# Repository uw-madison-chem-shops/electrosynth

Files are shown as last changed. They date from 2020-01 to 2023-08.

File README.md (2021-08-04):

# electrosynth 

Inexpensive circuits made for multi-channel electrochemical synthesis.
Galvanosynth: constant current driver.
Electrosynth: constant potential driver.

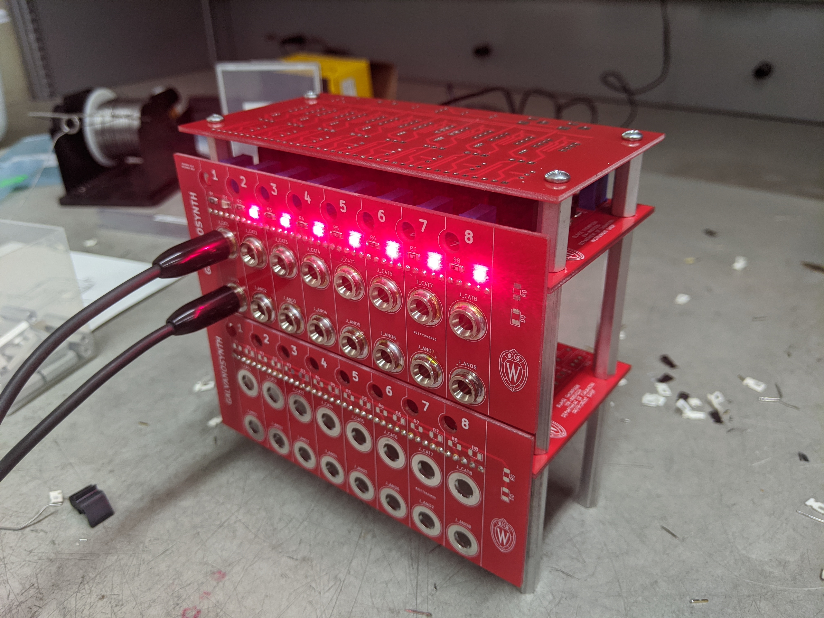
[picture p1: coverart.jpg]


## Repository

This is an open source hardware project licensed under the CERN Open Hardware Licence Version 2 - Permissive.
Please see the LICENSE file for the complete license.

This repository is being mirrored to several version control systems in an attempt to ensure maximum avaliability.

| name             | url                                                                  |
| ---------------- | -------------------------------------------------------------------- |
| blaise           | http://git.blaise.zone/uw-madison-chem-shops/electrosynth.git/about/ |
| Codeberg         | https://codeberg.org/uw-madison-chem-shops/electrosynth              |
| GitHub (primary) | https://github.com/uw-madison-chem-shops/electrosynth                |
| GitLab           | https://gitlab.com/uw-madison-chem-shops/electrosynth                |

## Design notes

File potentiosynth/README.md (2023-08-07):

# potentiosynth 

An inexpensive circuit made for driving multiple electrochemical constant potential reactions.



Each potentiosynth is made of three custom components:

- the main driver PCB
- the front panel PCB
- 3D printed bracket

See subdirectories for detailed instructions on each of these components.

## Bill of Materials

| reference      | value         | manufacturer  | part number          | vendors | # per Board |
| :------------- | :------------ | :------------ | :------------------- | :------ | :----------  |
| 40 Pin Header, Male, Right Angle | $0.00 | 3M | 2340-5111TG | Newark | 1 |
| 2" Standoff | $1.75 | Keystone Electronics | :------ | Newark | 4 |
| 0.625" Standoff | $0.50 | Keystone Electronics | :------ | Newark | 4 |

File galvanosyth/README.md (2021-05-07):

# galvanosynth

An inexpensive circuit made for driving multiple electrochemical constant current reactions.



Each galvanosynth is made of three custom components:

- the main driver PCB
- the front panel PCB
- 3D printed bracket

See subdirectories for detailed instructions on each of these components.

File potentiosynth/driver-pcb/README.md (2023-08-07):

# potentiosynth driver-pcb

An inexpensive circuit made for driving multiple electrochemical constant potential reactions.

## PCB

This PCB was designed using [KiCAD](https://www.kicad.org/) version 5.
Refer to [potentiosynth.pdf](./potentiosynth.pdf) for schematic. 
PCB images generated with [tracespace](https://github.com/tracespace/tracespace) follow.




## Bill of Materials

| reference      | value         | manufacturer  | part number          | vendors | # Per Board |
| :------------- | :------------ | :------------ | :------------------- | :------ | :--------- |
| 3/8 ˝ Square Trimpot® Trimming Potentiometer | $3.00 | Bourns | 3296X-1-202LF | DigiKey | 8 |
| Low-power Operational Amplifier  | $2.00  | Texas Instruments | TLV9154IDR | DigiKey | 8 |
| Fuse Block  | $3.00  | Littelfuse | 01550900M | DigiKey | 1 |
| 1 Amp Fuse  | $2.00  | Littelfuse | 0451001.MRL | DigiKey | 1 |
| PC TEST POINT MULTIPURPOSE RED  | $0.50  | Keystone Electronics | 5010 | Newark | 1 |
| PC TEST POINT MULTIPURPOSE BLACK  | $0.50  | Keystone Electronics | 5011 | Newark | 1 |
| Barrel Jack - 2.1 mm  | $0.50  | CUI | PJ-002A | DigiKey | 2 |
| 1/4W 4x 1k Resistors - 1206 | :------ | :------------ | :-------------- | :------ | 8 |
| 1/4W 4x 100k Resistors - 1206 | :------ | :------------ | :-------------- | :------ | 8 |
| 100 nF Capacitor - 1206 | :------ | :------------ | :-------------- | :------ | 1 |
| 330 nF Capacitor - 1206 | :------ | :------------ | :-------------- | :------ | 1 |
| 100 uF Capacitor - 1206 | :------ | :------------ | :-------------- | :------ | 1 |
| 1 uF Capacitor - 1206 | :------ | :------------ | :-------------- | :------ | 8 |
| R-7B15 - 0.5 | :------ | :------------ | :-------------- | :------ | 1 |

All prices are extended.
PCB itself should cost around $5.

## Changelog

### Unprinted

### Revision C

Added
- capacitor makes error detection better when unloaded
- bipolar error detection

### Revision B

Changed
- added fuse

Fixed
- added buffer amplifier since the differential amplifier drew too much current from reference

### Revision A 

Changed
- initial design

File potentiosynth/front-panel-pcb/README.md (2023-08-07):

# potentiosynth front-panel-pcb

An inexpensive circuit made for driving multiple electrochemical constant potential reactions.

## PCB

This PCB was designed using [KiCAD](https://www.kicad.org/) version 5.
Refer to [front-panel.pdf](./front-panel.pdf) for schematic. 
PCB images generated with [tracespace](https://github.com/tracespace/tracespace) follow.




## Bill of Materials

| reference      | value         | manufacturer  | part number          | vendors | # per Board |
| :------------- | :------------ | :------------ | :------------------- | :------ | :----------  |
| Banana Jack Board Mount | $1.00 | Keystone Electronics | 575-4 | Newark | 24 |
| 40 Pin Header, Male, Right Angle | $0.00 | 3M | 2340-5111TG | N/A | 1 (Cut down to 3 pins)  |
| 0.1" Jumper - 2 Position | $0.00 | Multicomp | MC-2228CG | N/A | 1 |
| 1/4W 1k Resistors - 1206 | :----- | :------------ | :-------- | :------ | 11 |
| SMT LEDs - 1206 | :----- | :------------ | :-------- | :------ | 11  |

All prices are extended.
PCB itself should cost around $5.

## Changelog

### Unprinted

## Fixed
- fixed silkscreen labels for oxidation and reduction

### Revision A 

## Changed
- initial design

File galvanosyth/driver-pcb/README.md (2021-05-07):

# galvanosynth driver-pcb

An inexpensive circuit made for driving multiple electrochemical constant current reactions.

## PCB

This PCB was designed using [KiCAD](https://www.kicad.org/) version 5.
Refer to [galvanosynth.pdf](./galvanosynth.pdf) for schematic. 
PCB images generated with [tracespace](https://github.com/tracespace/tracespace) follow.




## Bill of Materials

parts "per layer" for galvanosynth

| reference      | value         | manufacturer  | part number          | vendors |
| :------------- | :------------ | :------------ | :------------------- | :------ |
| trim pot, 2k                | 3296X-1-202LF       | 2.50 |     8 | 20.00 |         |
| banana jack                 | 575-4               | 1.00 |    16 | 16.00 |         |
| transistor, power           | IRF630              | 1.50 |     8 | 12.00 |         |
| PCB, mother                 | (custom)            | 6.00 |     1 |  6.00 |         |
| PCB, daughter               | (custom)            | 6.00 |     1 |  6.00 |         |
| standoff, 2", stacking      | 4558-440-AL         | 1.50 |     4 |  6.00 |         |
| op amp                      | LM358AP             | 0.50 |     8 |  4.00 |         |
| transistor, signal          | 2N7000              | 0.25 |     8 |  4.00 |         |
| bracket                     | (3D printed)        | 2.00 |     2 |  4.00 |         |
| trim pot, 1k                | 3296X-1-102LF       | 2.50 |     1 |  2.50 |         |
| barrel jack                 | PJ-002A             | 1.00 |     2 |  2.00 |         |
| LED, red                    | LTST-C230KRKT       | 0.25 |     8 |  2.00 |         |
| 100 uF                      | C3216X5R1A107M160AC | 1.25 |     1 |  1.25 |         |
| header, 40 pin, right angle | PRPC040SGAN-M71RC   | 1.00 |     1 |  1.00 |         |
| voltage regulator           | L7815CV             | 0.50 |     1 |  0.50 |         |
| test point, red             | 5010                | 0.50 |     1 |  0.50 |         |
| test point, white           | 5012                | 0.50 |     1 |  0.50 |         |
| test point, yellow          | 5014                | 0.50 |     1 |  0.50 |         |
| 330 nF                      | CC1206JRX7R9BB334   | 0.25 |     1 |  0.25 |         |
| LED, green                  | LTST-C150GKT        | 0.25 |     1 |  0.25 |         |
| 100 nF                      | CC1206KRX7R9BB104   | 0.10 |     1 |  0.10 |         |
| 10 kΩ                       | RC1206FR-0710KL     | 0.00 |     1 |  0.00 |         |
| 47 Ω                        | RC1206FR-0747RL     | 0.00 |     1 |  0.00 |         |
| 1 kΩ                        | RC1206FR-071KL      | 0.00 |    24 |  0.00 |         |
| 100 kΩ                      | RC1206FR-07100KL    | 0.00 |    16 |  0.00 |         |
| 10 Ω                        | RC1206FR-0710RL     | 0.00 |     8 |  0.00 |         |

All prices are extended.
PCB itself should cost around $5.

## Changelog

### Unprinted

### Revision D 

Changed
- initial design

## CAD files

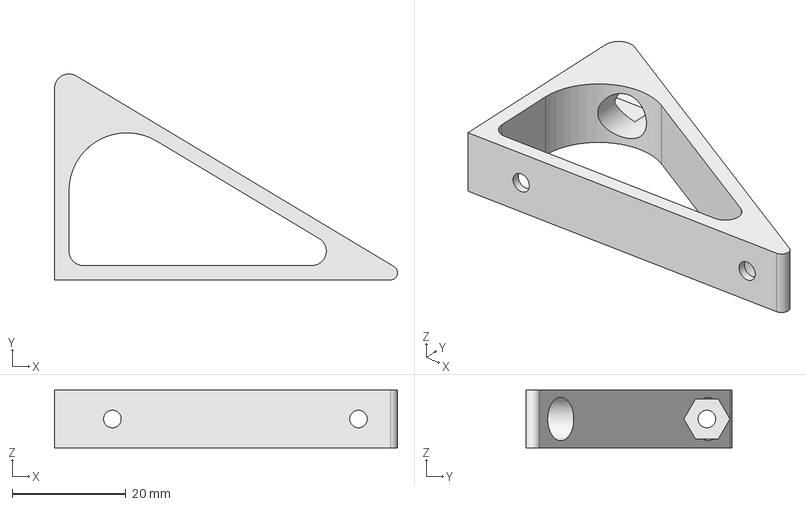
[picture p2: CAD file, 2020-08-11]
potentiosynth/bracket/bracket.FCStd
60.2 x 36.2 x 10.2 mm

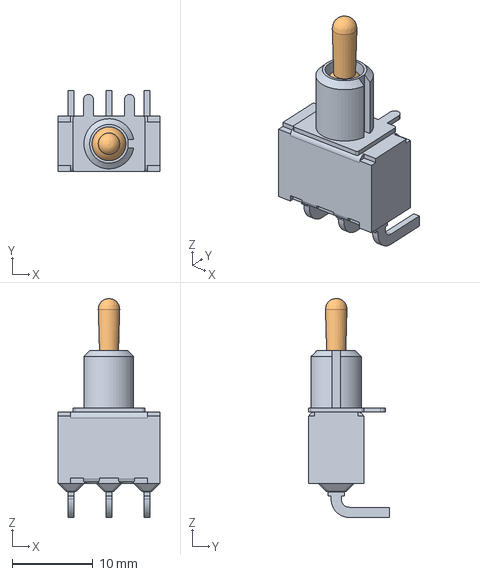
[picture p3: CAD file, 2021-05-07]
potentiosynth/front-panel-pcb/kicad/models/100SP1T2B4M6QE.step
12.7 x 10.0 x 27.2 mm

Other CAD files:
potentiosynth/bracket/bracket.stl

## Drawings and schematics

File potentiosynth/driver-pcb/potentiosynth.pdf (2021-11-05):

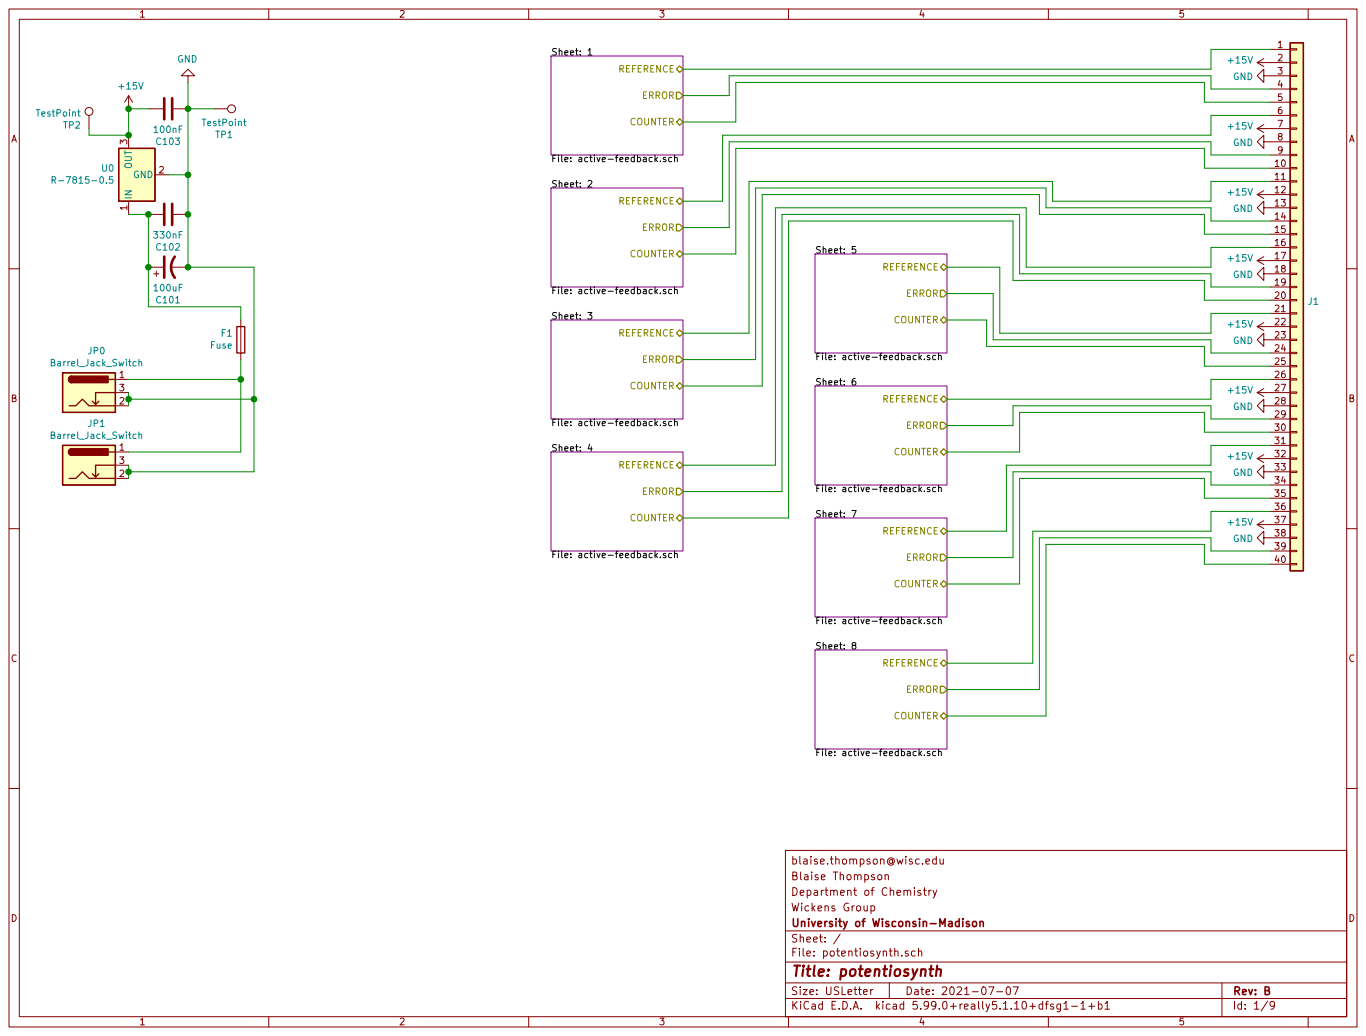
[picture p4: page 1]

Sheet: 1 File: active-feedback.schERROR

Sheet: 2 File: active-feedback.schERROR

Sheet: 5 File: active-feedback.schERROR
blaise.thompson@wisc.edu Sheet: 7 File: active-feedback.schERROR

Sheet: 3 File: active-feedback.schERROR

Sheet: 6 File: active-feedback.schERROR

Sheet: 4 File: active-feedback.schERROR

Sheet: 8 File: active-feedback.schERROR

Blaise Thompson
Department of Chemistry
Wickens Group
File: potentiosynth.sch Sheet: / University of Wisconsin-Madison

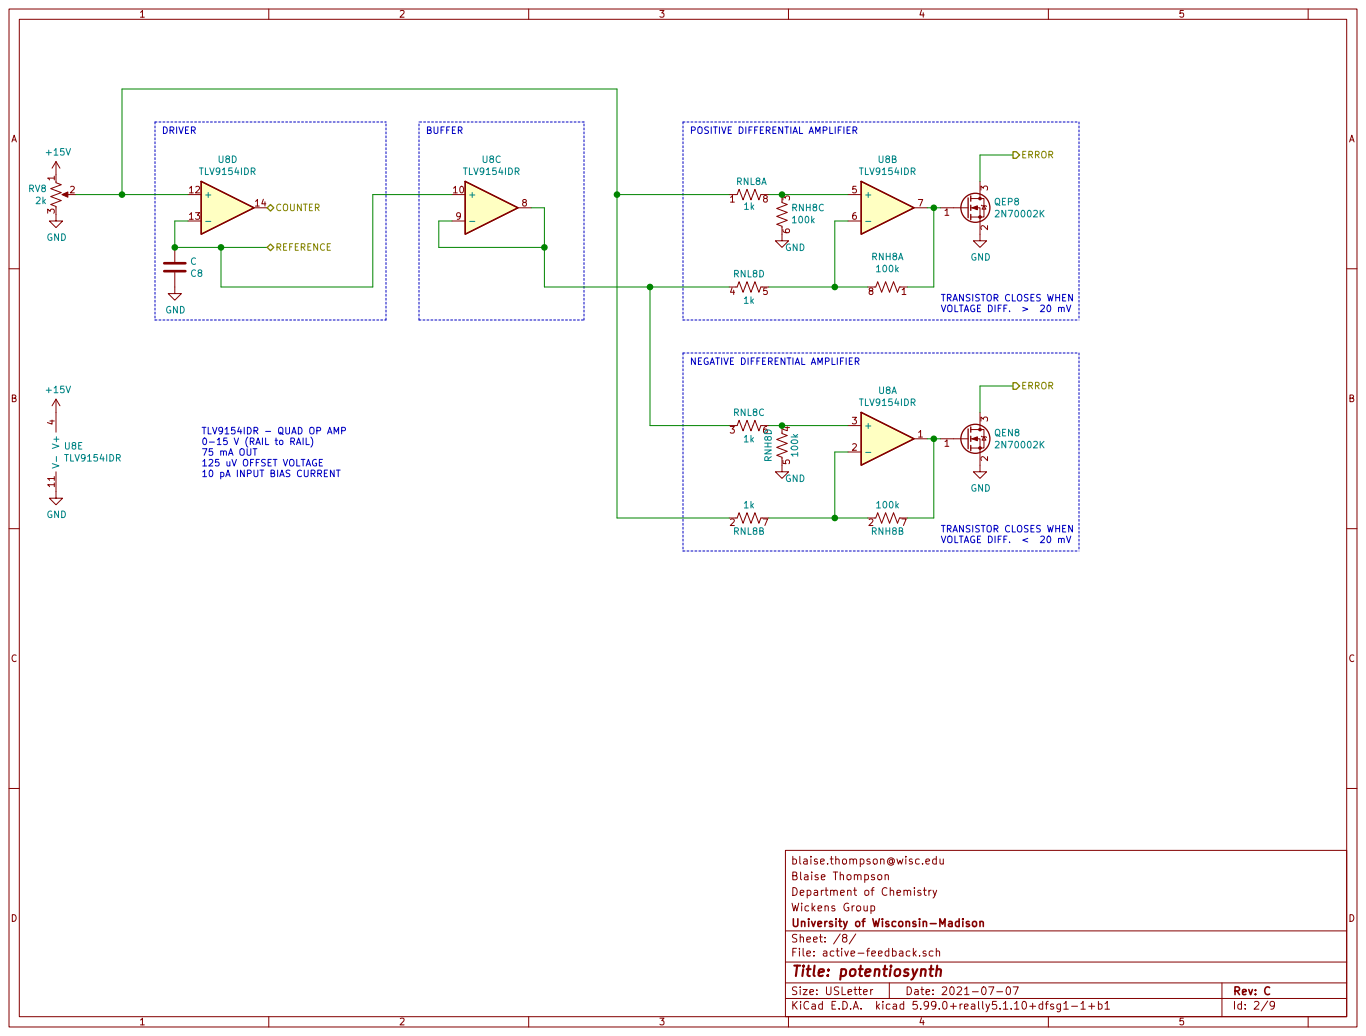
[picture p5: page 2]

TRANSISTOR CLOSES WHEN
VOLTAGE DIFF. > 20 mV TRANSISTOR CLOSES WHEN

VOLTAGE DIFF. < 20 mV TLV9154IDR - QUAD OP AMP
0-15 V (RAIL to RAIL) 75 mA OUT

Blaise Thompson
Department of Chemistry
Wickens Group
File: active-feedback.sch Sheet: /8/ University of Wisconsin-Madison

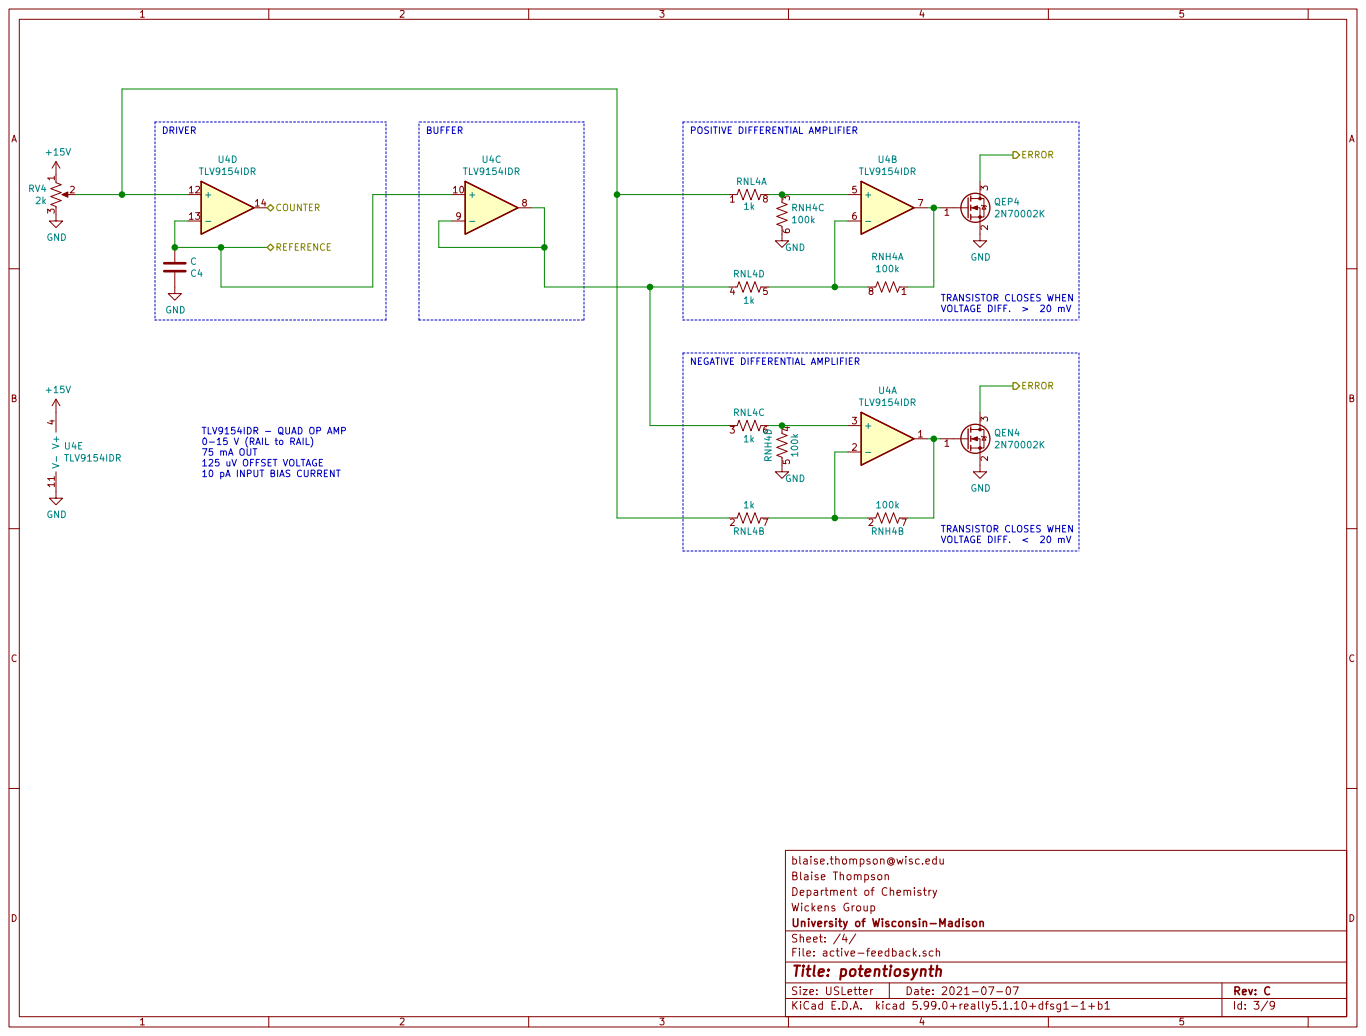
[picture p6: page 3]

TRANSISTOR CLOSES WHEN
VOLTAGE DIFF. > 20 mV TRANSISTOR CLOSES WHEN

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

Blaise Thompson
Department of Chemistry
Wickens Group
File: active-feedback.sch Sheet: /4/ University of Wisconsin-Madison

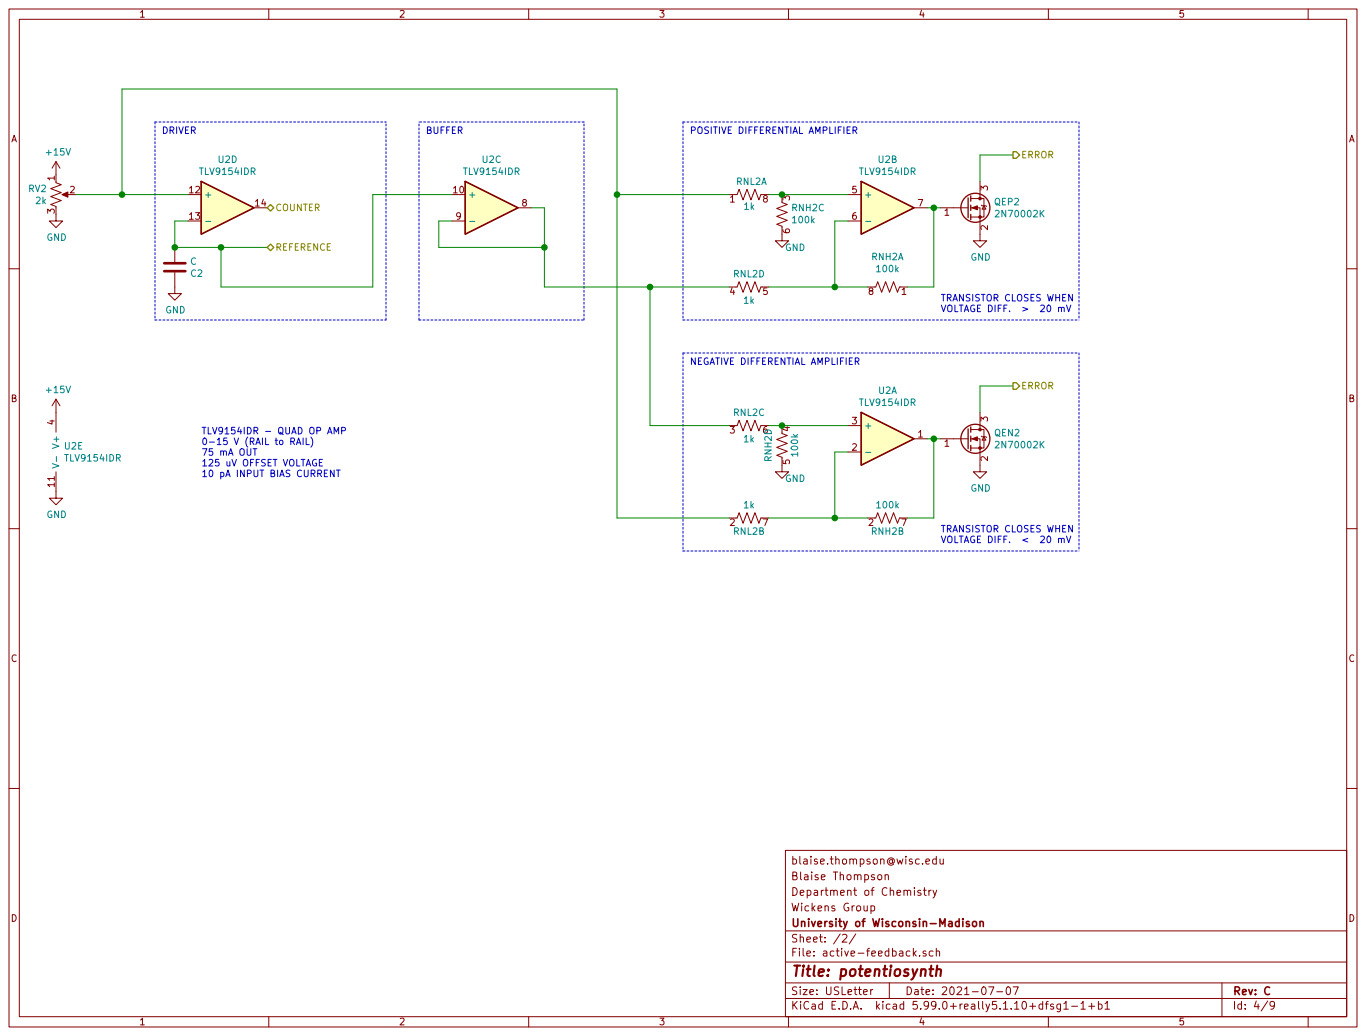
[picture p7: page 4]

TRANSISTOR CLOSES WHEN
VOLTAGE DIFF. > 20 mV TRANSISTOR CLOSES WHEN

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

Blaise Thompson
Department of Chemistry
Wickens Group
File: active-feedback.sch Sheet: /2/ University of Wisconsin-Madison

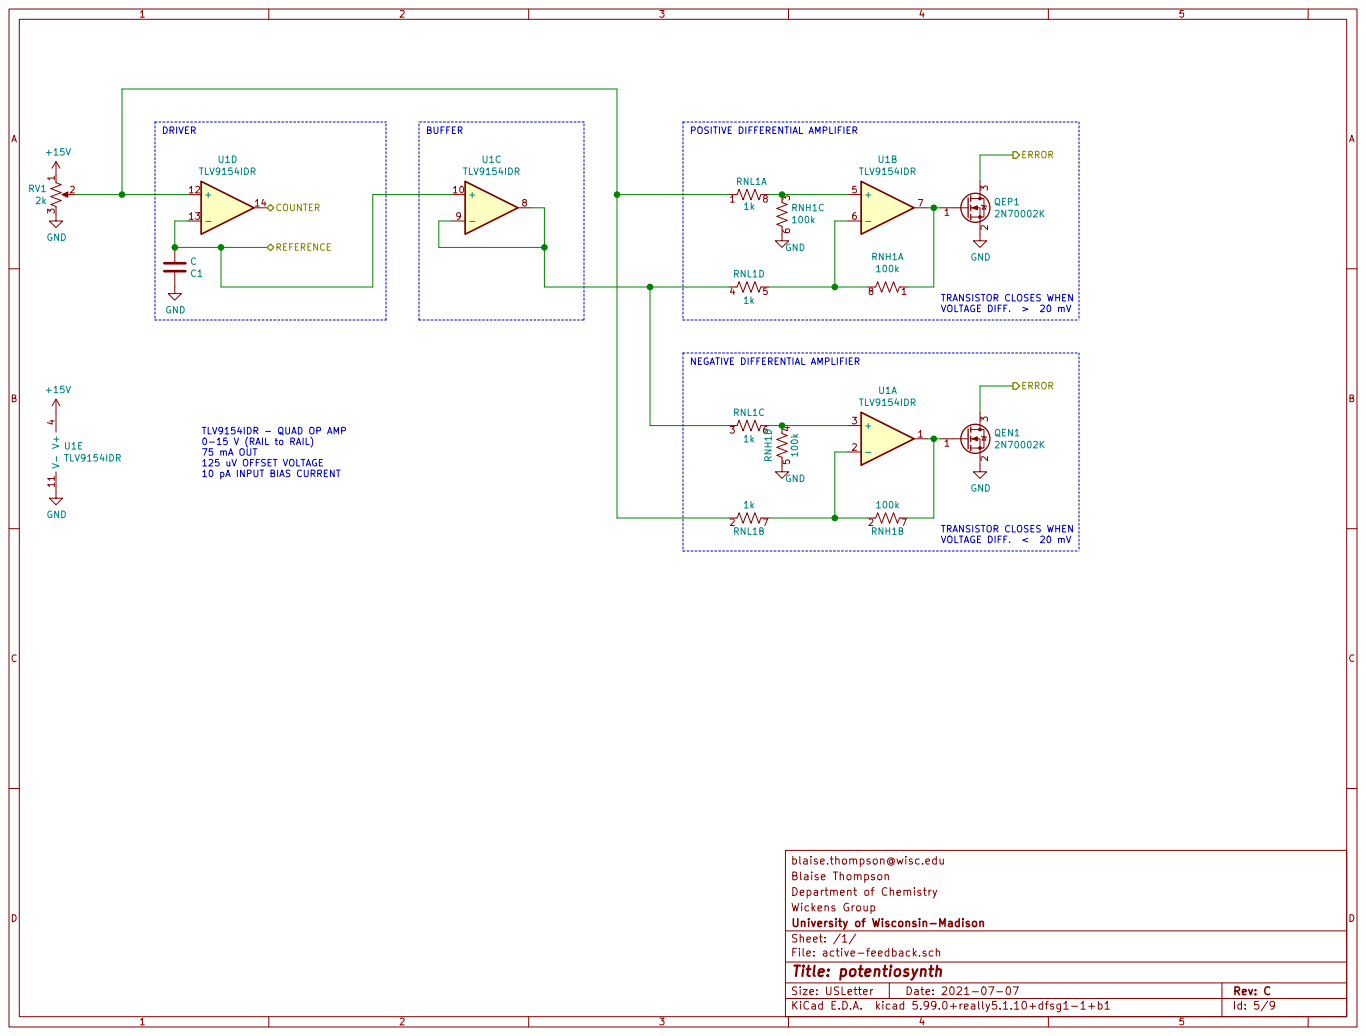
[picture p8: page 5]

TRANSISTOR CLOSES WHEN
VOLTAGE DIFF. > 20 mV TRANSISTOR CLOSES WHEN

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

Blaise Thompson
Department of Chemistry
Wickens Group
File: active-feedback.sch Sheet: /1/ University of Wisconsin-Madison

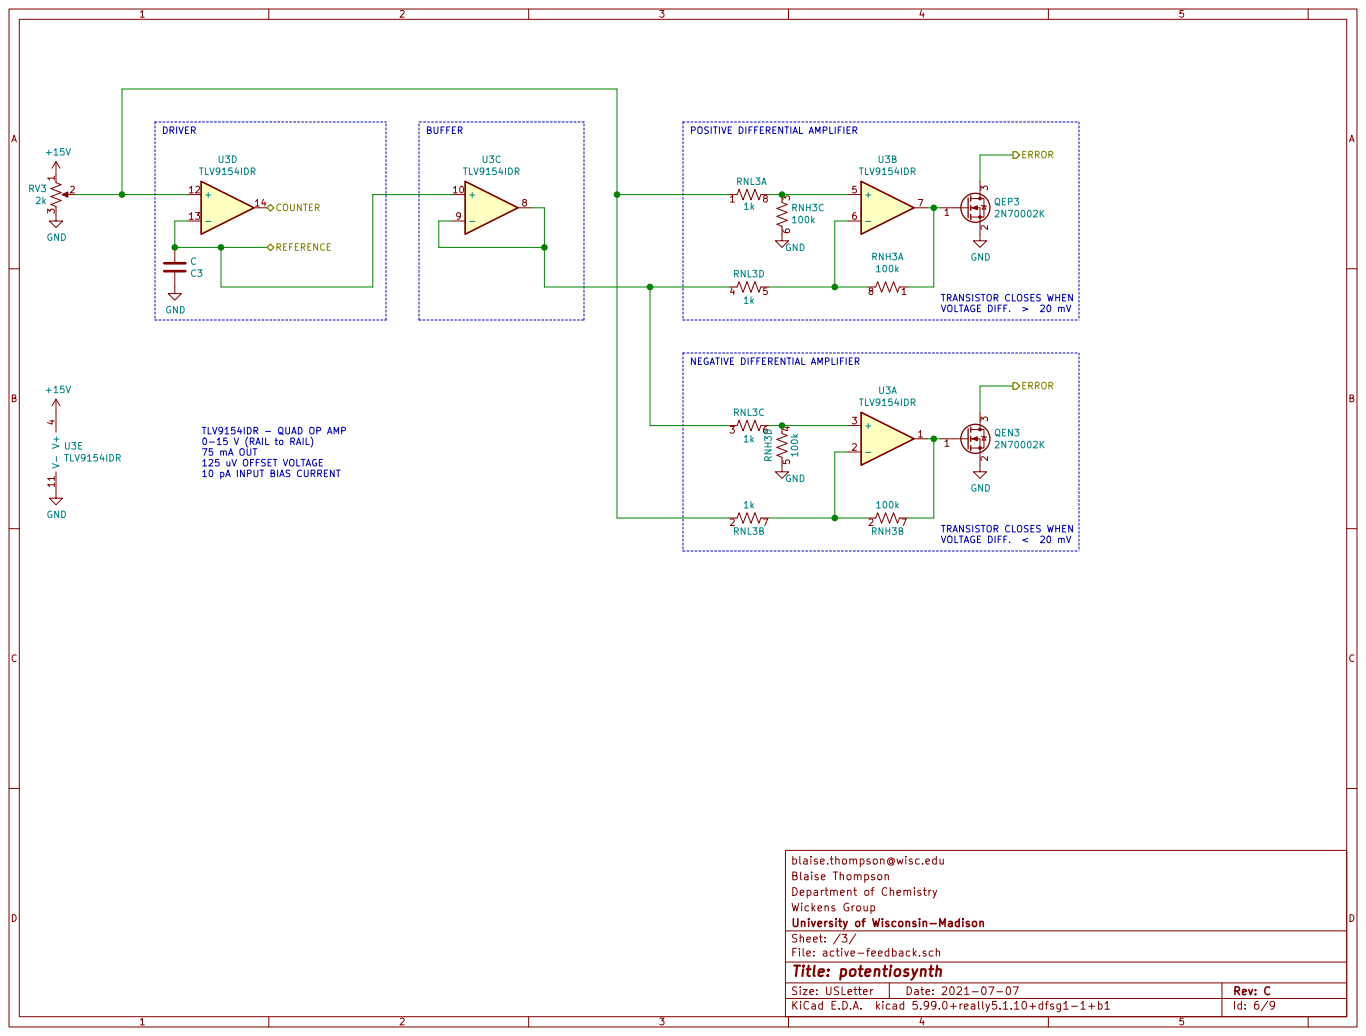
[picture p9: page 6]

TRANSISTOR CLOSES WHEN
VOLTAGE DIFF. > 20 mV TRANSISTOR CLOSES WHEN

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

Blaise Thompson
Department of Chemistry
Wickens Group
File: active-feedback.sch Sheet: /3/ University of Wisconsin-Madison

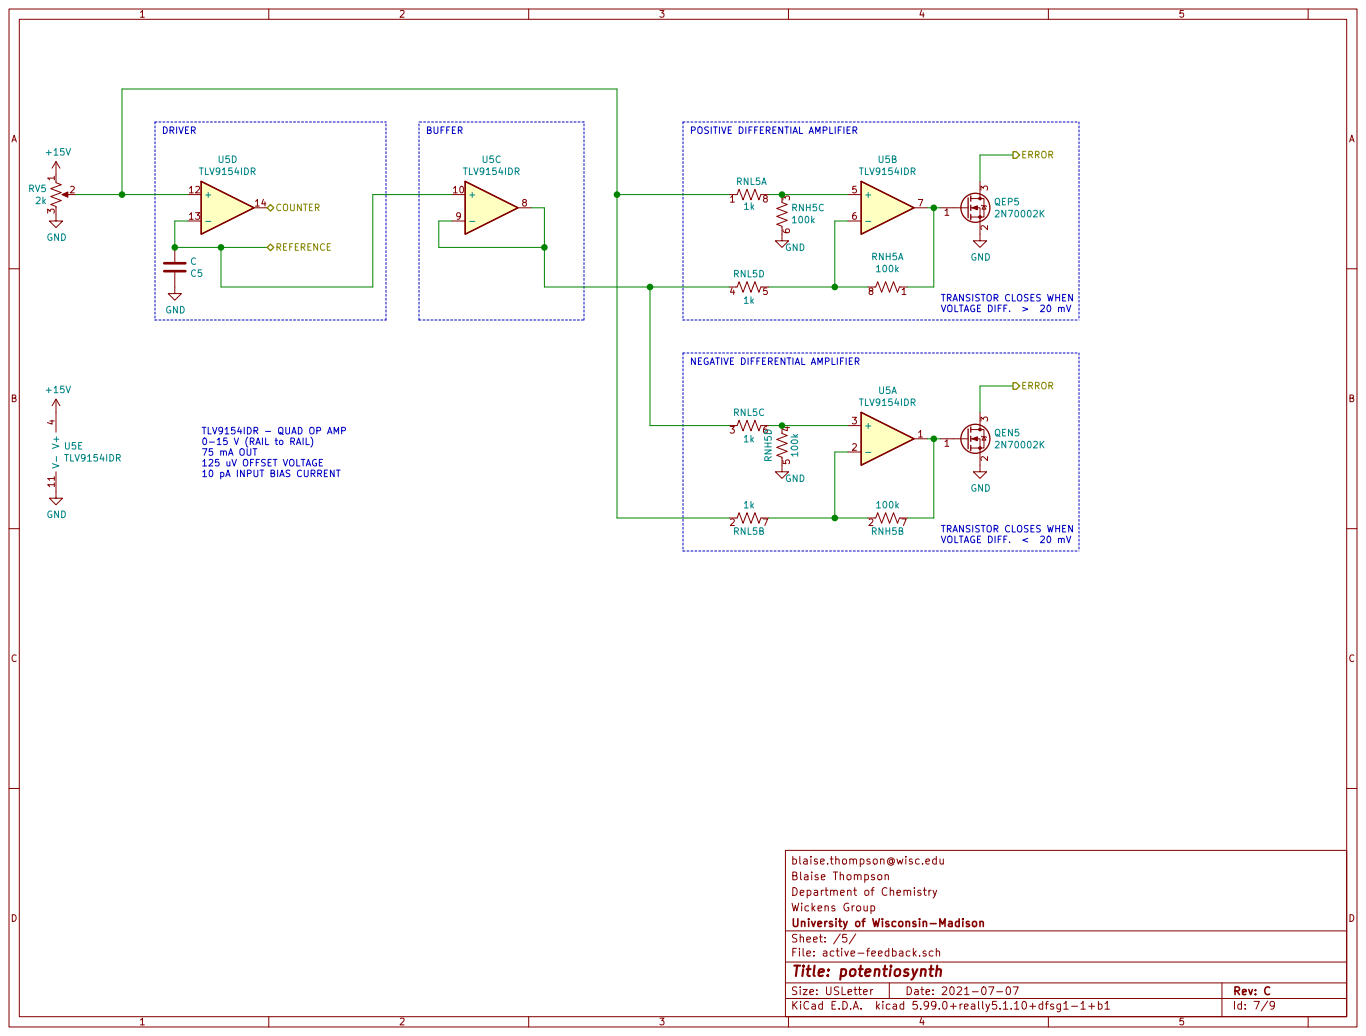
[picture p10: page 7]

TRANSISTOR CLOSES WHEN
VOLTAGE DIFF. > 20 mV TRANSISTOR CLOSES WHEN

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

Blaise Thompson
Department of Chemistry
Wickens Group
File: active-feedback.sch Sheet: /5/ University of Wisconsin-Madison

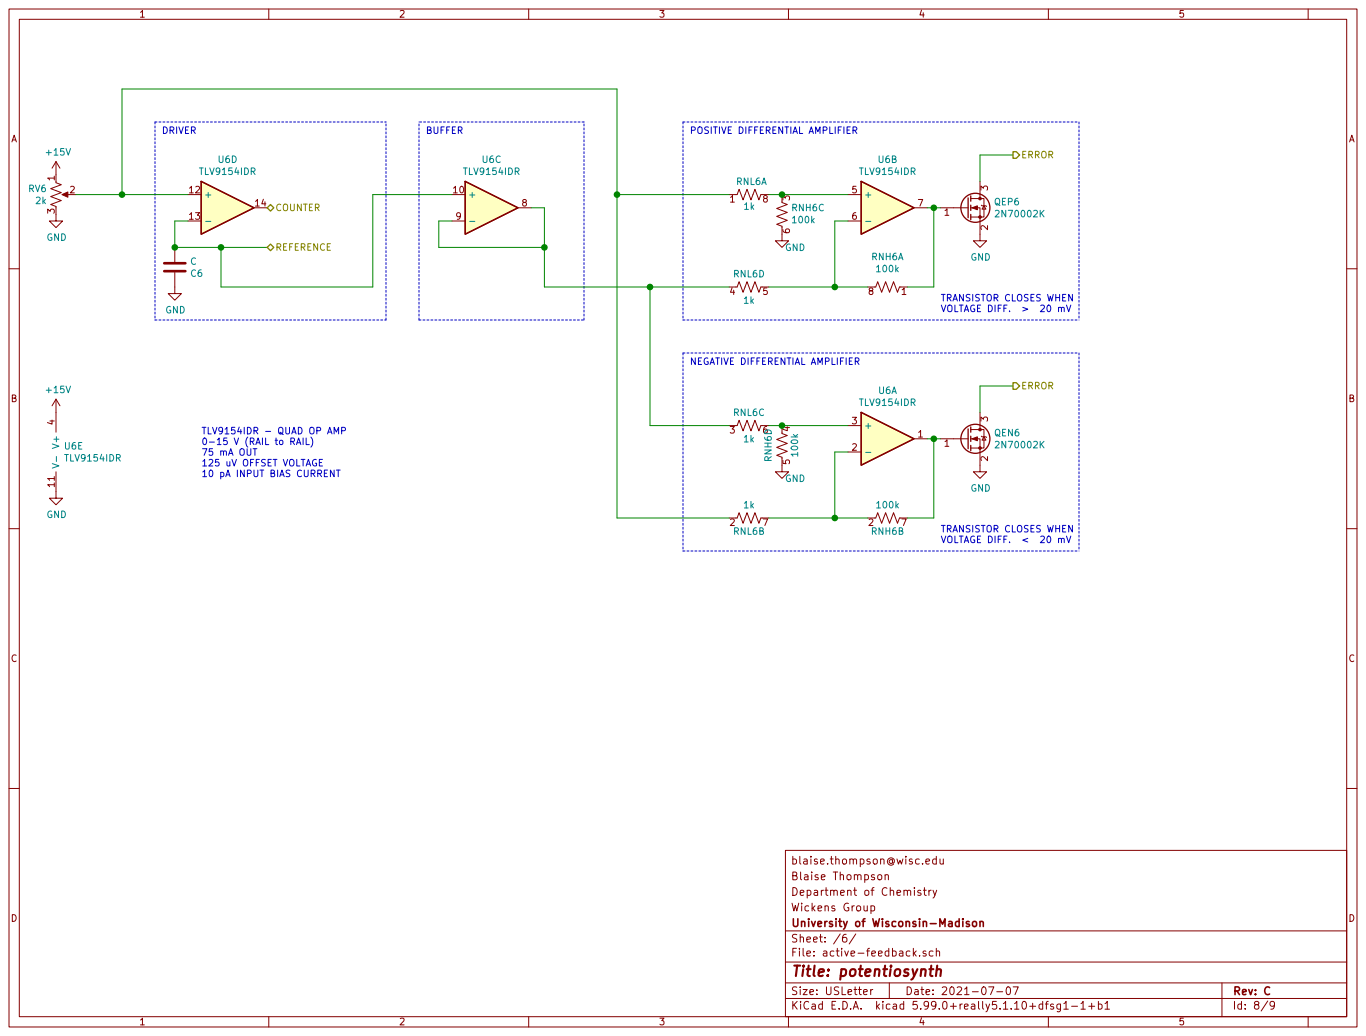
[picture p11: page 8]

TRANSISTOR CLOSES WHEN
VOLTAGE DIFF. > 20 mV TRANSISTOR CLOSES WHEN

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

Blaise Thompson
Department of Chemistry
Wickens Group
File: active-feedback.sch Sheet: /6/ University of Wisconsin-Madison

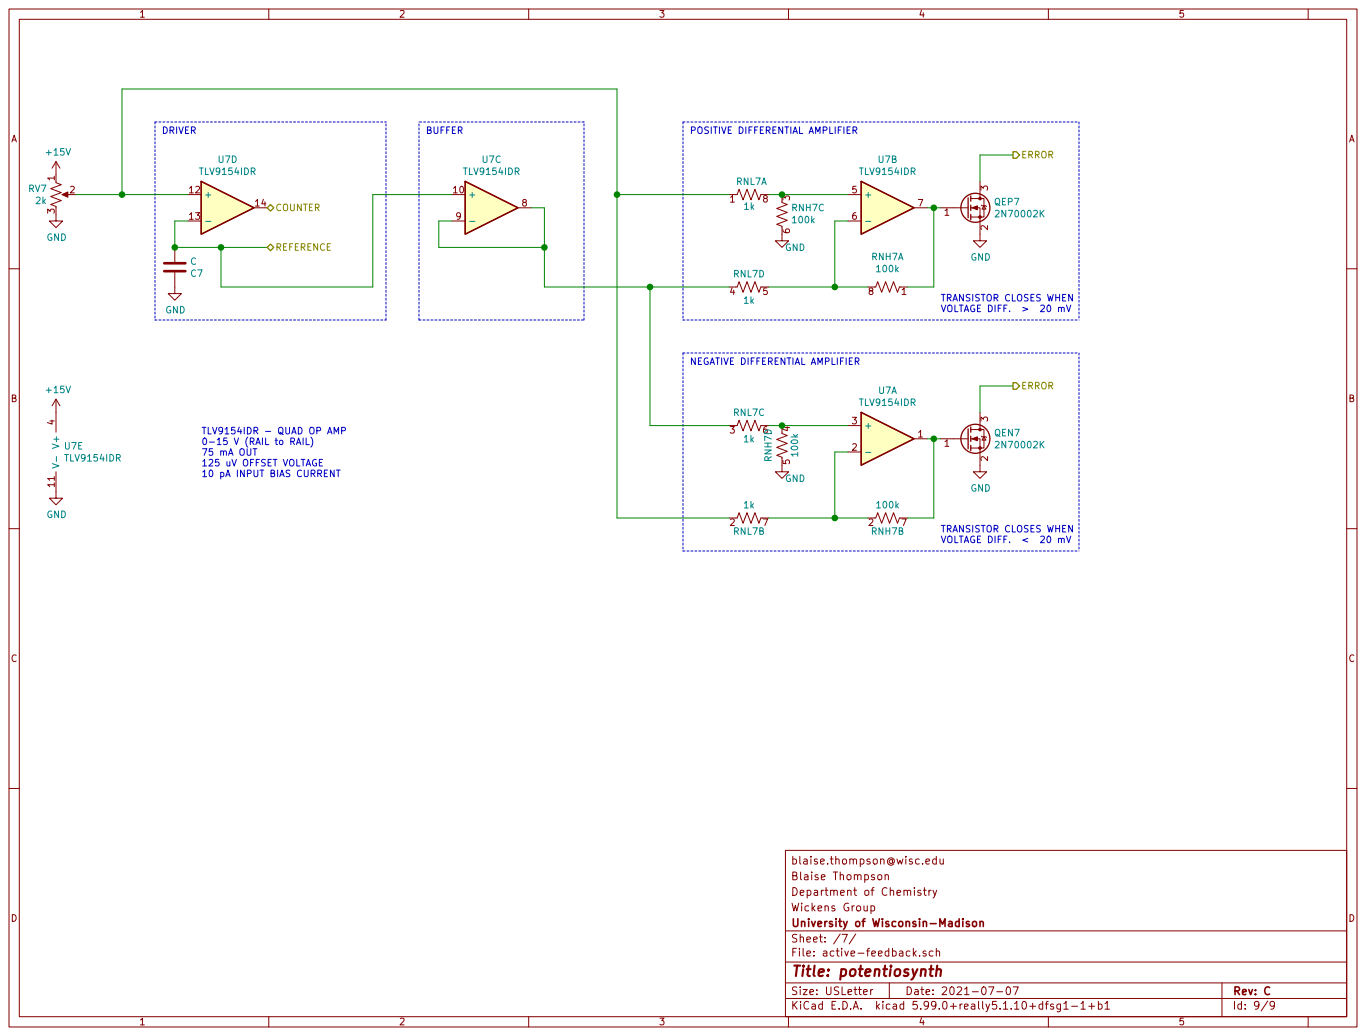
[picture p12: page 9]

TRANSISTOR CLOSES WHEN
VOLTAGE DIFF. > 20 mV TRANSISTOR CLOSES WHEN

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

Blaise Thompson
Department of Chemistry
Wickens Group
File: active-feedback.sch Sheet: /7/ University of Wisconsin-Madison

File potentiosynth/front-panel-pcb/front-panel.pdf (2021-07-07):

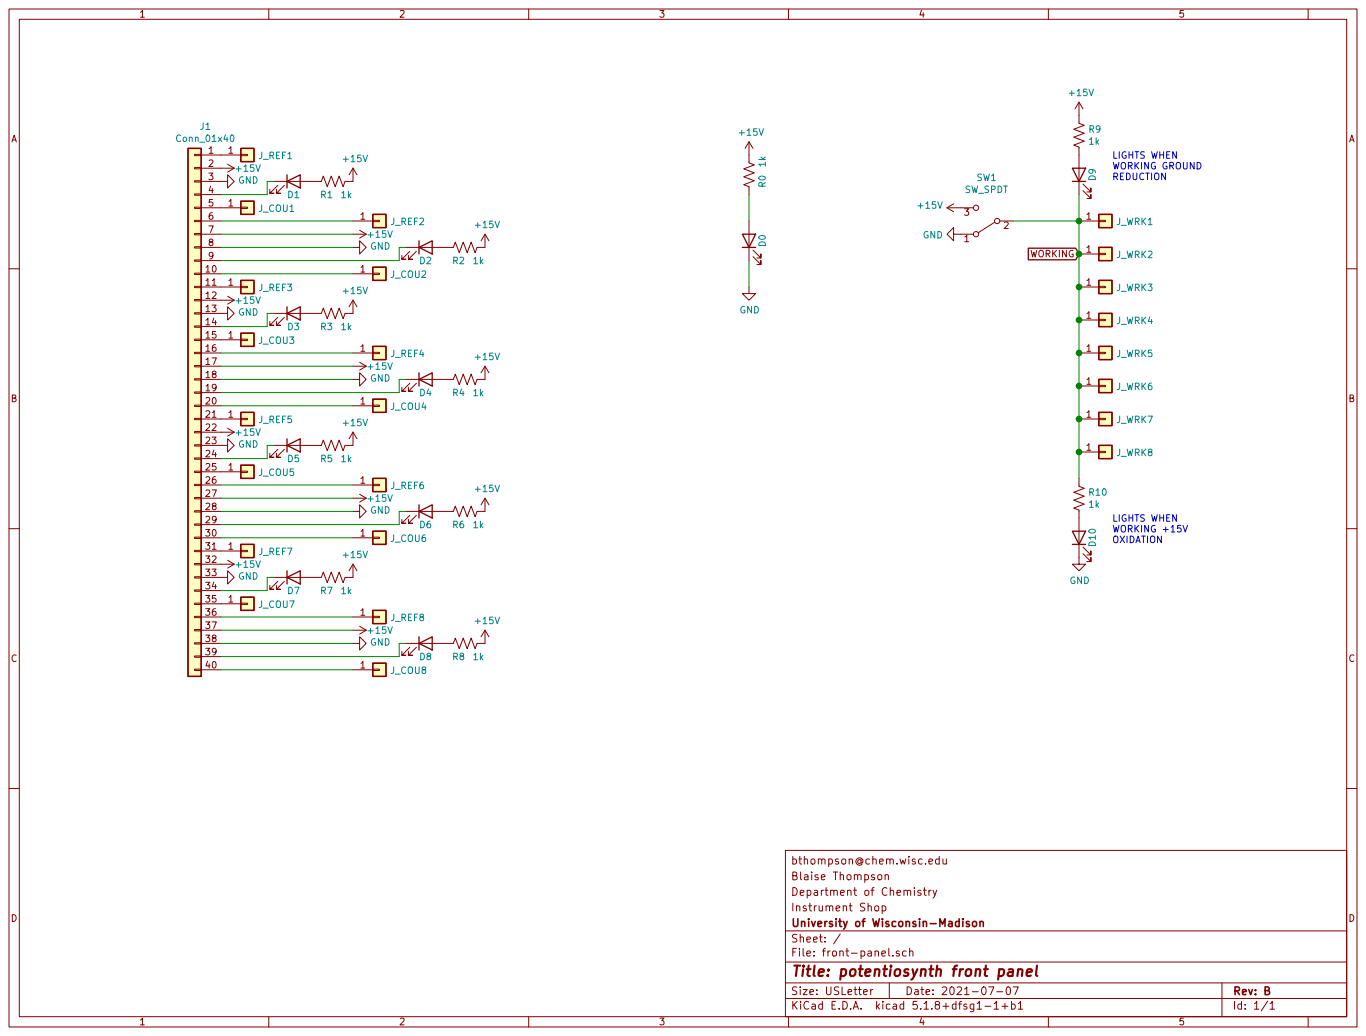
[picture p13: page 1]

LIGHTS WHEN WORKING GROUND

LIGHTS WHEN WORKING +15V OXIDATION

Blaise Thompson
Department of Chemistry
Instrument Shop
File: front-panel.sch Sheet: / University of Wisconsin-Madison

Id: 1/1 Title: potentiosynth front panel

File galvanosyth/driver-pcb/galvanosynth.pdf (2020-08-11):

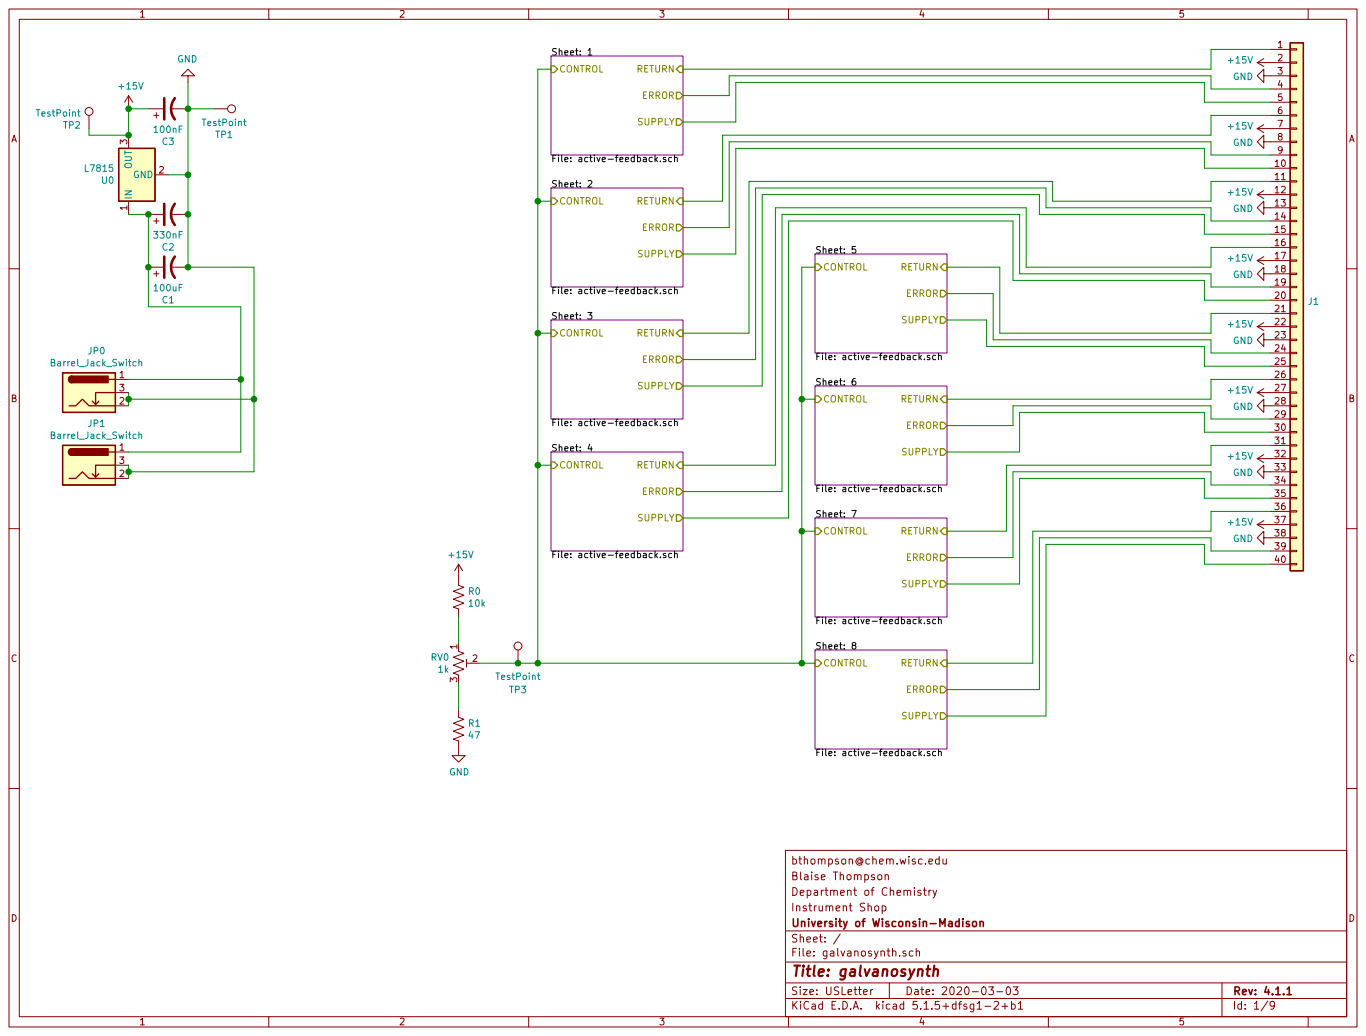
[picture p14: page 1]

GND GND GND GND 123

bthompson@chem.wisc.edu
Blaise Thompson
Department of Chemistry
Instrument Shop
File: galvanosynth.sch Sheet: / University of Wisconsin-Madison

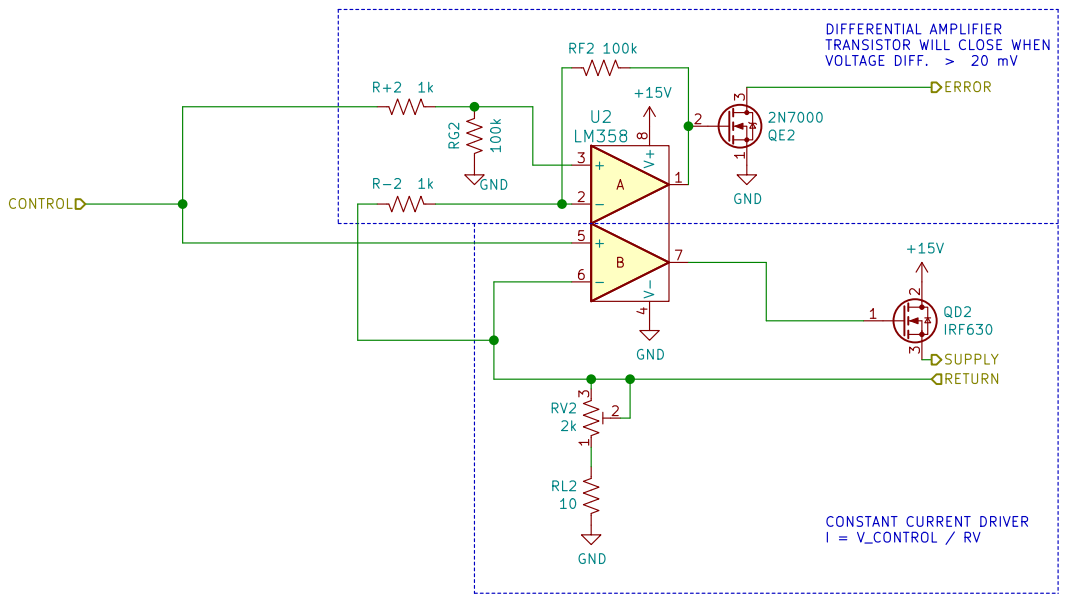
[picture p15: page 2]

TRANSISTOR WILL CLOSE WHEN
VOLTAGE DIFF. > 20 mV CONSTANT CURRENT DRIVER

bthompson@chem.wisc.edu RL2

Blaise Thompson
Department of Chemistry
Instrument Shop
File: active-feedback.sch Sheet: /2/ University of Wisconsin-Madison


TRANSISTOR WILL CLOSE WHEN
VOLTAGE DIFF. > 20 mV CONSTANT CURRENT DRIVER

bthompson@chem.wisc.edu RL6

Blaise Thompson
Department of Chemistry
Instrument Shop
File: active-feedback.sch Sheet: /6/ University of Wisconsin-Madison


TRANSISTOR WILL CLOSE WHEN
VOLTAGE DIFF. > 20 mV CONSTANT CURRENT DRIVER

bthompson@chem.wisc.edu RL7

Blaise Thompson
Department of Chemistry
Instrument Shop
File: active-feedback.sch Sheet: /7/ University of Wisconsin-Madison


TRANSISTOR WILL CLOSE WHEN
VOLTAGE DIFF. > 20 mV CONSTANT CURRENT DRIVER

bthompson@chem.wisc.edu RL8

Blaise Thompson
Department of Chemistry
Instrument Shop
File: active-feedback.sch Sheet: /8/ University of Wisconsin-Madison


TRANSISTOR WILL CLOSE WHEN
VOLTAGE DIFF. > 20 mV CONSTANT CURRENT DRIVER

bthompson@chem.wisc.edu RL5

Blaise Thompson
Department of Chemistry
Instrument Shop
File: active-feedback.sch Sheet: /5/ University of Wisconsin-Madison


TRANSISTOR WILL CLOSE WHEN
VOLTAGE DIFF. > 20 mV CONSTANT CURRENT DRIVER

bthompson@chem.wisc.edu RL3

Blaise Thompson
Department of Chemistry
Instrument Shop
File: active-feedback.sch Sheet: /3/ University of Wisconsin-Madison


TRANSISTOR WILL CLOSE WHEN
VOLTAGE DIFF. > 20 mV CONSTANT CURRENT DRIVER

bthompson@chem.wisc.edu RL4

Blaise Thompson
Department of Chemistry
Instrument Shop
File: active-feedback.sch Sheet: /4/ University of Wisconsin-Madison


TRANSISTOR WILL CLOSE WHEN
VOLTAGE DIFF. > 20 mV CONSTANT CURRENT DRIVER

bthompson@chem.wisc.edu RL1

Blaise Thompson
Department of Chemistry
Instrument Shop
File: active-feedback.sch Sheet: /1/ University of Wisconsin-Madison

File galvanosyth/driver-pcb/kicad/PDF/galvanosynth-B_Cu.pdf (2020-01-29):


bthompson@chem.wisc.edu
Blaise Thompson
Instrument Shop
Department of Chemistry
File: galvanosynth.kicad_pcb Sheet: University of Wisconsin-Madison

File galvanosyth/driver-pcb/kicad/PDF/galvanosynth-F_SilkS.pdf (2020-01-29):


Blaise Thompson
Instrument Shop
Department of Chemistry
File: galvanosynth.kicad_pcb Sheet: University of Wisconsin-Madison

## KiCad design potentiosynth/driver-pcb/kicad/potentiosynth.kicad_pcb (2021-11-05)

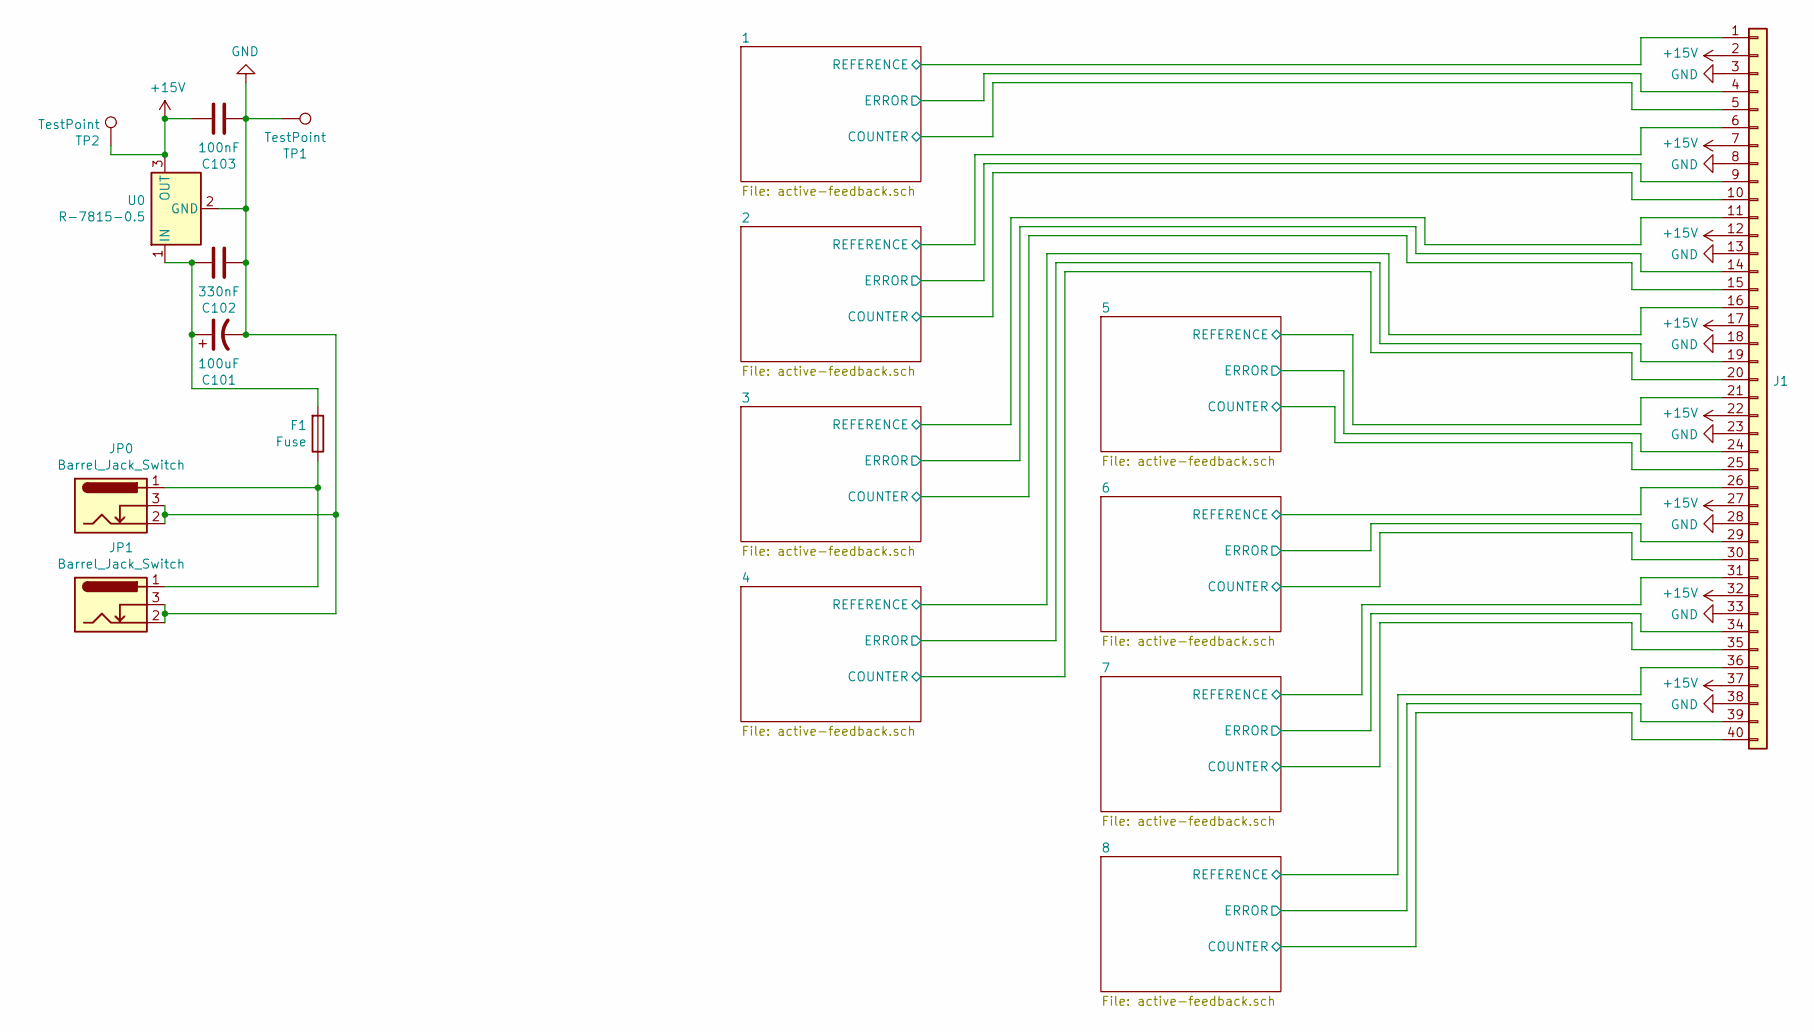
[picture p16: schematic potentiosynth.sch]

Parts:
C101: 100uF; CP_Radial_Tantal_D7.0mm_P2.50mm
C102: 330nF; C_1206_3216Metric_Pad1.33x1.80mm_HandSolder
C103: 100nF; C_1206_3216Metric_Pad1.33x1.80mm_HandSolder
F1: Fuse; 01550900M
J1: Conn_01x40; PinHeader_1x40_P2.54mm_Horizontal
JP0, JP1: Barrel_Jack_Switch; BarrelJack_Horizontal
TP1, TP2: TestPoint; TestPoint_THTPad_D3.0mm_Drill1.5mm
U0: R-7815-0.5; CONV_VXO7815-500-M

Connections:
+15V: C103.1, J1.2, J1.7, J1.12, J1.17, J1.22, J1.27, J1.32, J1.37, TP2.1, U0.3 (OUT); also elsewhere on the board
/1/COUNTER: J1.5; also elsewhere on the board
/1/ERROR: J1.4; also elsewhere on the board
/1/REFERENCE: J1.1; also elsewhere on the board
/2/COUNTER: J1.10; also elsewhere on the board
/2/ERROR: J1.9; also elsewhere on the board
/2/REFERENCE: J1.6; also elsewhere on the board
/3/COUNTER: J1.15; also elsewhere on the board
/3/ERROR: J1.14; also elsewhere on the board
/3/REFERENCE: J1.11; also elsewhere on the board
/4/COUNTER: J1.20; also elsewhere on the board
/4/ERROR: J1.19; also elsewhere on the board
/4/REFERENCE: J1.16; also elsewhere on the board
/5/COUNTER: J1.25; also elsewhere on the board
/5/ERROR: J1.24; also elsewhere on the board
/5/REFERENCE: J1.21; also elsewhere on the board
/6/COUNTER: J1.30; also elsewhere on the board
/6/ERROR: J1.29; also elsewhere on the board
/6/REFERENCE: J1.26; also elsewhere on the board
/7/COUNTER: J1.35; also elsewhere on the board
/7/ERROR: J1.34; also elsewhere on the board
/7/REFERENCE: J1.31; also elsewhere on the board
/8/COUNTER: J1.40; also elsewhere on the board
/8/ERROR: J1.39; also elsewhere on the board
/8/REFERENCE: J1.36; also elsewhere on the board
GND: C101.2, C102.2, C103.2, J1.3, J1.8, J1.13, J1.18, J1.23, J1.28, J1.33, J1.38, JP0.2, JP0.3, JP1.2, JP1.3, TP1.1, U0.2 (GND); also elsewhere on the board
unnamed: C101.1, C102.1, F1.2, U0.1 (IN)
unnamed: F1.1, JP0.1, JP1.1

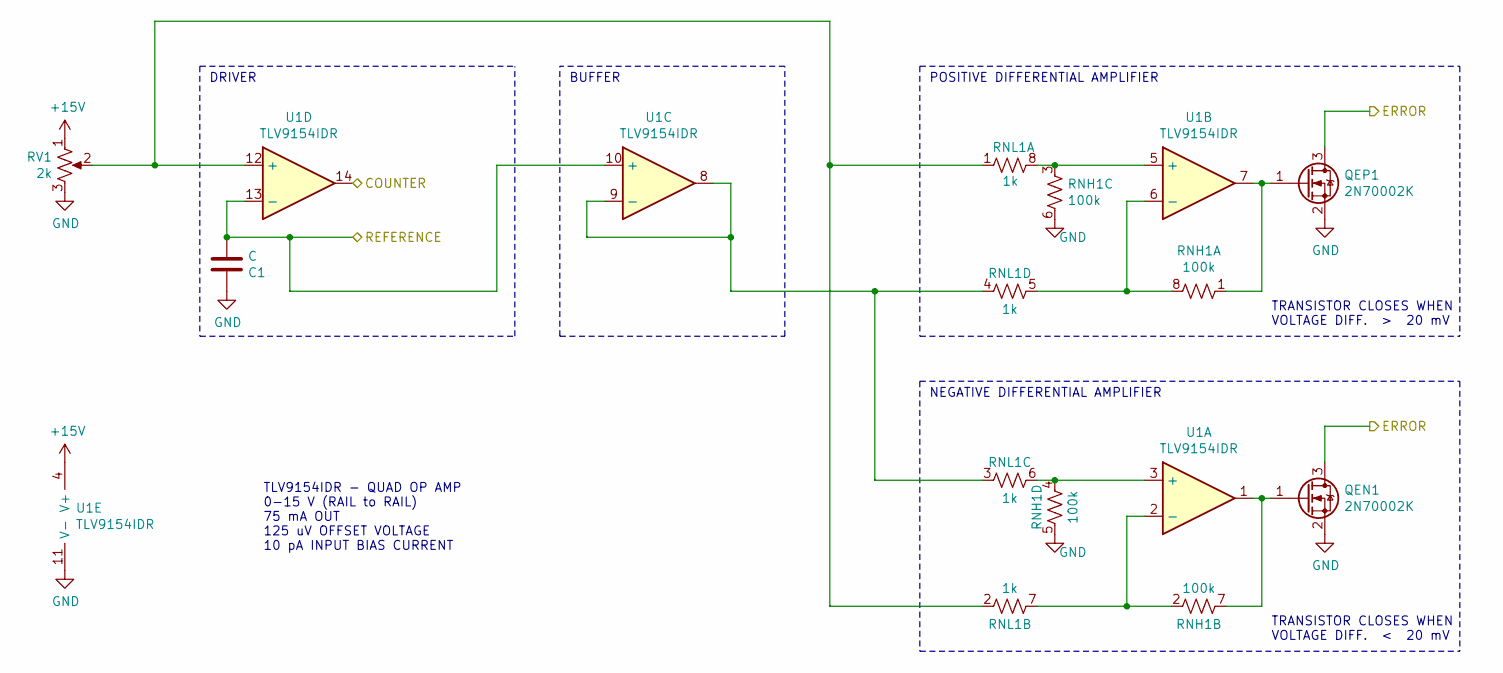
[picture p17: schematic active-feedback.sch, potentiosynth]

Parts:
C1: C; C_1206_3216Metric_Pad1.33x1.80mm_HandSolder
QEN1: 2N70002K; SOT-23_Handsoldering
QEP1: 2N70002K; SOT-23_Handsoldering
RNH1: 100k; CAY16-104J4LF
RNL1: 1k; CAY16-104J4LF
RV1: 2k; Potentiometer_Bourns_3296X_Horizontal
U1: TLV9154IDR; SOIC-14_3.9x8.7mm_P1.27mm

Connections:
+15V: RV1.1, U1.4 (V+); also elsewhere on the board
/1/COUNTER: U1.14; also elsewhere on the board
/1/ERROR: QEN1.3 (D), QEP1.3 (D); also elsewhere on the board
/1/REFERENCE: C1.1, U1.10 (+), U1.13 (-); also elsewhere on the board
GND: C1.2, QEN1.2 (S), QEP1.2 (S), RNH1.5 (R4.2), RNH1.6 (R3.2), RV1.3, U1.11 (V-); also elsewhere on the board
unnamed: QEN1.1 (G), RNH1.7 (R2.2), U1.1
unnamed: QEP1.1 (G), RNH1.1 (R1.1), U1.7
unnamed: RNH1.2 (R2.1), RNL1.7 (R2.2), U1.2 (-)
unnamed: RNH1.3 (R3.1), RNL1.8 (R1.2), U1.5 (+)
unnamed: RNH1.4 (R4.1), RNL1.6 (R3.2), U1.3 (+)
unnamed: RNH1.8 (R1.2), RNL1.5 (R4.2), U1.6 (-)
unnamed: RNL1.1 (R1.1), RNL1.2 (R2.1), RV1.2, U1.12 (+)
unnamed: RNL1.3 (R3.1), RNL1.4 (R4.1), U1.8, U1.9 (-)

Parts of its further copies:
C2, C3, C4, C5, C6, C7, C8: C; C_1206_3216Metric_Pad1.33x1.80mm_HandSolder
QEN2, QEN3, QEN4, QEN5, QEN6, QEN7, QEN8: 2N70002K; SOT-23_Handsoldering
QEP2, QEP3, QEP4, QEP5, QEP6, QEP7, QEP8: 2N70002K; SOT-23_Handsoldering
RNH2, RNH3, RNH4, RNH5, RNH6, RNH7, RNH8: 100k; CAY16-104J4LF
RNL2, RNL3, RNL4, RNL5, RNL6, RNL7, RNL8: 1k; CAY16-104J4LF
RV2, RV3, RV4, RV5, RV6, RV7, RV8: 2k; Potentiometer_Bourns_3296X_Horizontal
U2, U3, U4, U5, U6, U7, U8: TLV9154IDR; SOIC-14_3.9x8.7mm_P1.27mm

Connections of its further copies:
+15V: RV2.1, RV3.1, RV4.1, RV5.1, RV6.1, RV7.1, RV8.1, U2.4 (V+), U3.4 (V+), U4.4 (V+), U5.4 (V+), U6.4 (V+), U7.4 (V+), U8.4 (V+); also elsewhere on the board
/2/COUNTER: U2.14; also elsewhere on the board
/2/ERROR: QEN2.3 (D), QEP2.3 (D); also elsewhere on the board
/2/REFERENCE: C2.1, U2.10 (+), U2.13 (-); also elsewhere on the board
/3/COUNTER: U3.14; also elsewhere on the board
/3/ERROR: QEN3.3 (D), QEP3.3 (D); also elsewhere on the board
/3/REFERENCE: C3.1, U3.10 (+), U3.13 (-); also elsewhere on the board
/4/COUNTER: U4.14; also elsewhere on the board
/4/ERROR: QEN4.3 (D), QEP4.3 (D); also elsewhere on the board
/4/REFERENCE: C4.1, U4.10 (+), U4.13 (-); also elsewhere on the board
/5/COUNTER: U5.14; also elsewhere on the board
/5/ERROR: QEN5.3 (D), QEP5.3 (D); also elsewhere on the board
/5/REFERENCE: C5.1, U5.10 (+), U5.13 (-); also elsewhere on the board
/6/COUNTER: U6.14; also elsewhere on the board
/6/ERROR: QEN6.3 (D), QEP6.3 (D); also elsewhere on the board
/6/REFERENCE: C6.1, U6.10 (+), U6.13 (-); also elsewhere on the board
/7/COUNTER: U7.14; also elsewhere on the board
/7/ERROR: QEN7.3 (D), QEP7.3 (D); also elsewhere on the board
/7/REFERENCE: C7.1, U7.10 (+), U7.13 (-); also elsewhere on the board
/8/COUNTER: U8.14; also elsewhere on the board
/8/ERROR: QEN8.3 (D), QEP8.3 (D); also elsewhere on the board
/8/REFERENCE: C8.1, U8.10 (+), U8.13 (-); also elsewhere on the board
GND: C2.2, C3.2, C4.2, C5.2, C6.2, C7.2, C8.2, QEN2.2 (S), QEN3.2 (S), QEN4.2 (S), QEN5.2 (S), QEN6.2 (S), QEN7.2 (S), QEN8.2 (S), QEP2.2 (S), QEP3.2 (S), QEP4.2 (S), QEP5.2 (S), QEP6.2 (S), QEP7.2 (S), QEP8.2 (S), RNH2.5 (R4.2), RNH2.6 (R3.2), RNH3.5 (R4.2), RNH3.6 (R3.2), RNH4.5 (R4.2), RNH4.6 (R3.2), RNH5.5 (R4.2), RNH5.6 (R3.2), RNH6.5 (R4.2), RNH6.6 (R3.2), RNH7.5 (R4.2), RNH7.6 (R3.2), RNH8.5 (R4.2), RNH8.6 (R3.2), RV2.3, RV3.3, RV4.3, RV5.3, RV6.3, RV7.3, RV8.3, U2.11 (V-), U3.11 (V-), U4.11 (V-), U5.11 (V-), U6.11 (V-), U7.11 (V-), U8.11 (V-); also elsewhere on the board
unnamed: QEN2.1 (G), RNH2.7 (R2.2), U2.1
unnamed: QEN3.1 (G), RNH3.7 (R2.2), U3.1
unnamed: QEN4.1 (G), RNH4.7 (R2.2), U4.1
unnamed: QEN5.1 (G), RNH5.7 (R2.2), U5.1
unnamed: QEN6.1 (G), RNH6.7 (R2.2), U6.1
unnamed: QEN7.1 (G), RNH7.7 (R2.2), U7.1
unnamed: QEN8.1 (G), RNH8.7 (R2.2), U8.1
unnamed: QEP2.1 (G), RNH2.1 (R1.1), U2.7
unnamed: QEP3.1 (G), RNH3.1 (R1.1), U3.7
unnamed: QEP4.1 (G), RNH4.1 (R1.1), U4.7
unnamed: QEP5.1 (G), RNH5.1 (R1.1), U5.7
unnamed: QEP6.1 (G), RNH6.1 (R1.1), U6.7
unnamed: QEP7.1 (G), RNH7.1 (R1.1), U7.7
unnamed: QEP8.1 (G), RNH8.1 (R1.1), U8.7
unnamed: RNH2.2 (R2.1), RNL2.7 (R2.2), U2.2 (-)
unnamed: RNH2.3 (R3.1), RNL2.8 (R1.2), U2.5 (+)
unnamed: RNH2.4 (R4.1), RNL2.6 (R3.2), U2.3 (+)
unnamed: RNH2.8 (R1.2), RNL2.5 (R4.2), U2.6 (-)
unnamed: RNH3.2 (R2.1), RNL3.7 (R2.2), U3.2 (-)
unnamed: RNH3.3 (R3.1), RNL3.8 (R1.2), U3.5 (+)
unnamed: RNH3.4 (R4.1), RNL3.6 (R3.2), U3.3 (+)
unnamed: RNH3.8 (R1.2), RNL3.5 (R4.2), U3.6 (-)
unnamed: RNH4.2 (R2.1), RNL4.7 (R2.2), U4.2 (-)
unnamed: RNH4.3 (R3.1), RNL4.8 (R1.2), U4.5 (+)
unnamed: RNH4.4 (R4.1), RNL4.6 (R3.2), U4.3 (+)
unnamed: RNH4.8 (R1.2), RNL4.5 (R4.2), U4.6 (-)
unnamed: RNH5.2 (R2.1), RNL5.7 (R2.2), U5.2 (-)
unnamed: RNH5.3 (R3.1), RNL5.8 (R1.2), U5.5 (+)
unnamed: RNH5.4 (R4.1), RNL5.6 (R3.2), U5.3 (+)
unnamed: RNH5.8 (R1.2), RNL5.5 (R4.2), U5.6 (-)
unnamed: RNH6.2 (R2.1), RNL6.7 (R2.2), U6.2 (-)
unnamed: RNH6.3 (R3.1), RNL6.8 (R1.2), U6.5 (+)
unnamed: RNH6.4 (R4.1), RNL6.6 (R3.2), U6.3 (+)
unnamed: RNH6.8 (R1.2), RNL6.5 (R4.2), U6.6 (-)
unnamed: RNH7.2 (R2.1), RNL7.7 (R2.2), U7.2 (-)
unnamed: RNH7.3 (R3.1), RNL7.8 (R1.2), U7.5 (+)
unnamed: RNH7.4 (R4.1), RNL7.6 (R3.2), U7.3 (+)
unnamed: RNH7.8 (R1.2), RNL7.5 (R4.2), U7.6 (-)
unnamed: RNH8.2 (R2.1), RNL8.7 (R2.2), U8.2 (-)
unnamed: RNH8.3 (R3.1), RNL8.8 (R1.2), U8.5 (+)
unnamed: RNH8.4 (R4.1), RNL8.6 (R3.2), U8.3 (+)
unnamed: RNH8.8 (R1.2), RNL8.5 (R4.2), U8.6 (-)
unnamed: RNL2.1 (R1.1), RNL2.2 (R2.1), RV2.2, U2.12 (+)
unnamed: RNL2.3 (R3.1), RNL2.4 (R4.1), U2.8, U2.9 (-)
unnamed: RNL3.1 (R1.1), RNL3.2 (R2.1), RV3.2, U3.12 (+)
unnamed: RNL3.3 (R3.1), RNL3.4 (R4.1), U3.8, U3.9 (-)
unnamed: RNL4.1 (R1.1), RNL4.2 (R2.1), RV4.2, U4.12 (+)
unnamed: RNL4.3 (R3.1), RNL4.4 (R4.1), U4.8, U4.9 (-)
unnamed: RNL5.1 (R1.1), RNL5.2 (R2.1), RV5.2, U5.12 (+)
unnamed: RNL5.3 (R3.1), RNL5.4 (R4.1), U5.8, U5.9 (-)
unnamed: RNL6.1 (R1.1), RNL6.2 (R2.1), RV6.2, U6.12 (+)
unnamed: RNL6.3 (R3.1), RNL6.4 (R4.1), U6.8, U6.9 (-)
unnamed: RNL7.1 (R1.1), RNL7.2 (R2.1), RV7.2, U7.12 (+)
unnamed: RNL7.3 (R3.1), RNL7.4 (R4.1), U7.8, U7.9 (-)
unnamed: RNL8.1 (R1.1), RNL8.2 (R2.1), RV8.2, U8.12 (+)
unnamed: RNL8.3 (R3.1), RNL8.4 (R4.1), U8.8, U8.9 (-)

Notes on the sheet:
TRANSISTOR CLOSES WHEN VOLTAGE DIFF. > 20 mV
POSITIVE DIFFERENTIAL AMPLIFIER
BUFFER
DRIVER
TLV9154IDR - QUAD OP AMP 0-15 V (RAIL to RAIL) 75 mA OUT 125 uV OFFSET VOLTAGE 10 pA INPUT BIAS CURRENT
TRANSISTOR CLOSES WHEN VOLTAGE DIFF. < 20 mV
NEGATIVE DIFFERENTIAL AMPLIFIER

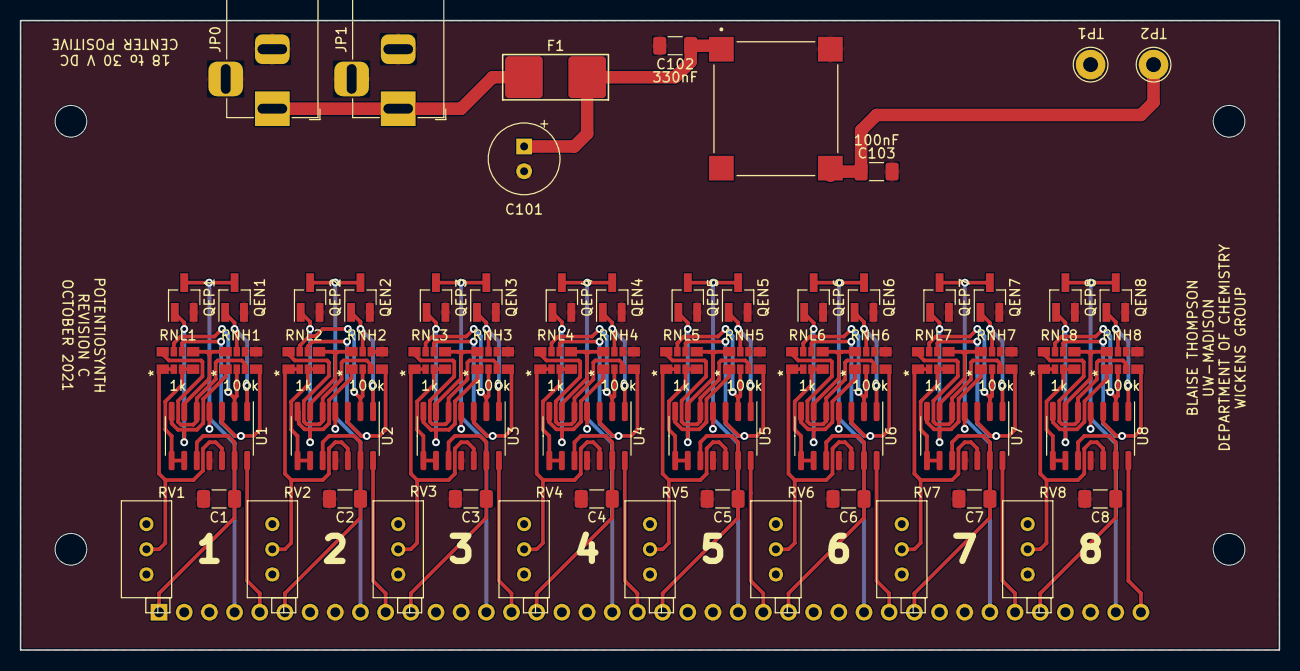
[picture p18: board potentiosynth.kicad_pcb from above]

Board: 2 copper layers, 127.0 x 63.5 mm, 66 parts (1 on the bottom side), 92 nets.

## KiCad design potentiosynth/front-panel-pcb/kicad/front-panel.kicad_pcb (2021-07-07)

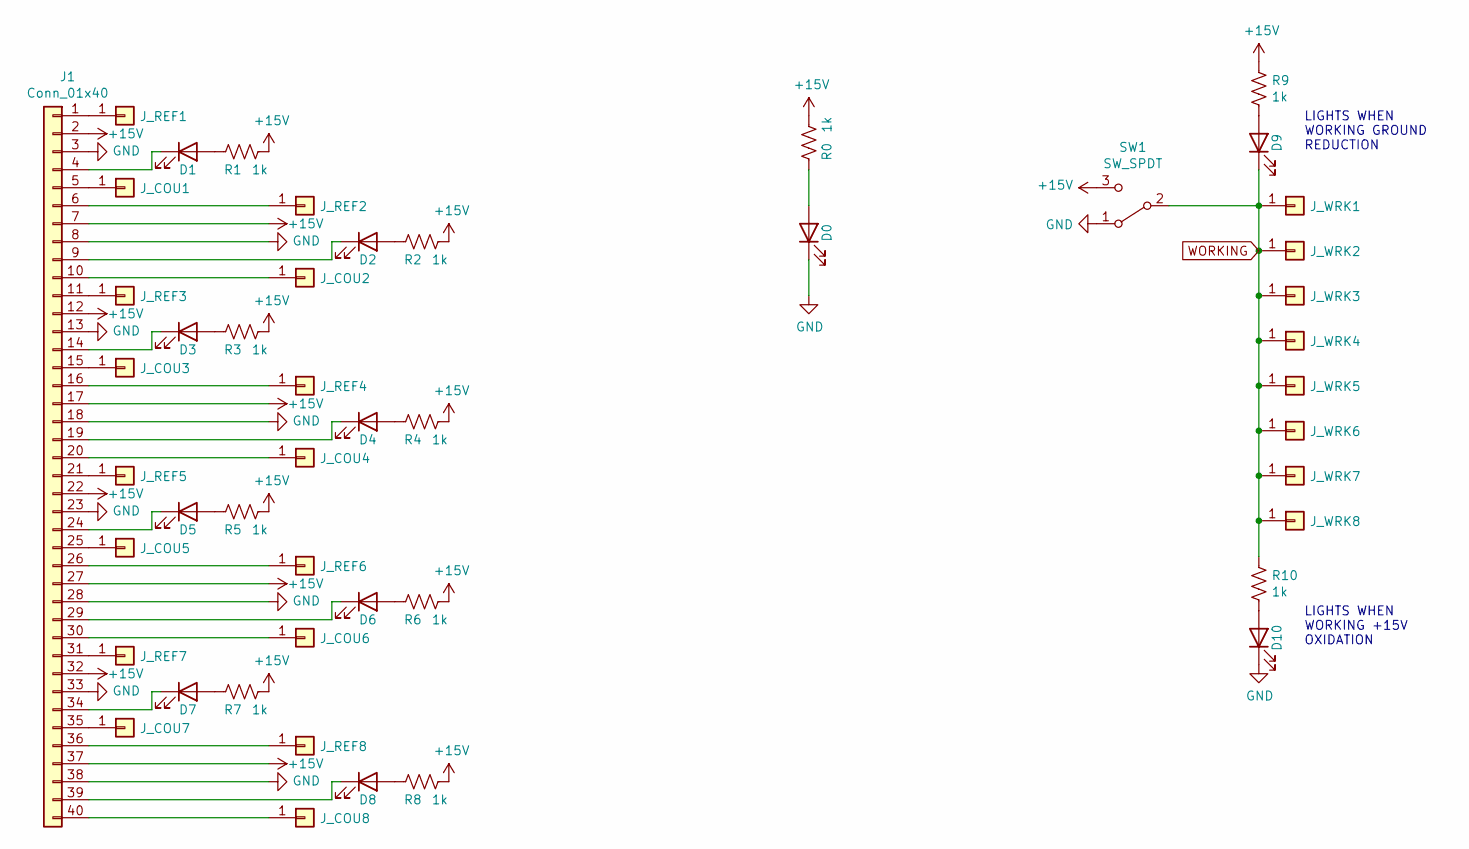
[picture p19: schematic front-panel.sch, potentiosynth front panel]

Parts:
D0, D1, D2, D3, D4, D5, D6, D7, D8, D9, D10: LED; D_1206_3216Metric
J1: Conn_01x40; PinHeader_1x40_P2.54mm_Vertical
J_COU1, J_COU2, J_COU3, J_COU4, J_COU5, J_COU6, J_COU7, J_COU8: Conn_01x01; Banana_Jack_1Pin
J_REF1, J_REF2, J_REF3, J_REF4, J_REF5, J_REF6, J_REF7, J_REF8: Conn_01x01; Banana_Jack_1Pin
J_WRK1, J_WRK2, J_WRK3, J_WRK4, J_WRK5, J_WRK6, J_WRK7, J_WRK8: Conn_01x01; Banana_Jack_1Pin
R0, R1, R2, R3, R4, R5, R6, R7, R8, R9, R10: 1k; R_1206_3216Metric
SW1: SW_SPDT; PinHeader_1x03_P2.54mm_Horizontal

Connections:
+15V: J1.2, J1.7, J1.12, J1.17, J1.22, J1.27, J1.32, J1.37, R0.1, R1.1, R2.1, R3.1, R4.1, R5.1, R6.1, R7.1, R8.1, R9.1, SW1.3 (C)
GND: D0.1 (K), D10.1 (K), J1.3, J1.8, J1.13, J1.18, J1.23, J1.28, J1.33, J1.38, SW1.1 (A)
unnamed: D0.2 (A), R0.2
unnamed: D1.1 (K), J1.4
unnamed: D1.2 (A), R1.2
unnamed: D2.1 (K), J1.9
unnamed: D2.2 (A), R2.2
unnamed: D3.1 (K), J1.14
unnamed: D3.2 (A), R3.2
unnamed: D4.1 (K), J1.19
unnamed: D4.2 (A), R4.2
unnamed: D5.1 (K), J1.24
unnamed: D5.2 (A), R5.2
unnamed: D6.1 (K), J1.29
unnamed: D6.2 (A), R6.2
unnamed: D7.1 (K), J1.34
unnamed: D7.2 (A), R7.2
unnamed: D8.1 (K), J1.39
unnamed: D8.2 (A), R8.2
unnamed: D9.2 (A), R9.2
unnamed: D10.2 (A), R10.2
unnamed: J1.1, J_REF1.1
unnamed: J1.5, J_COU1.1
unnamed: J1.6, J_REF2.1
unnamed: J1.10, J_COU2.1
unnamed: J1.11, J_REF3.1
unnamed: J1.15, J_COU3.1
unnamed: J1.16, J_REF4.1
unnamed: J1.20, J_COU4.1
unnamed: J1.21, J_REF5.1
unnamed: J1.25, J_COU5.1
unnamed: J1.26, J_REF6.1
unnamed: J1.30, J_COU6.1
unnamed: J1.31, J_REF7.1
unnamed: J1.35, J_COU7.1
unnamed: J1.36, J_REF8.1
unnamed: J1.40, J_COU8.1
WORKING: D9.1 (K), J_WRK1.1, J_WRK2.1, J_WRK3.1, J_WRK4.1, J_WRK5.1, J_WRK6.1, J_WRK7.1, J_WRK8.1, R10.1, SW1.2 (B)

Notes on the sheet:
LIGHTS WHEN WORKING GROUND REDUCTION
LIGHTS WHEN WORKING +15V OXIDATION

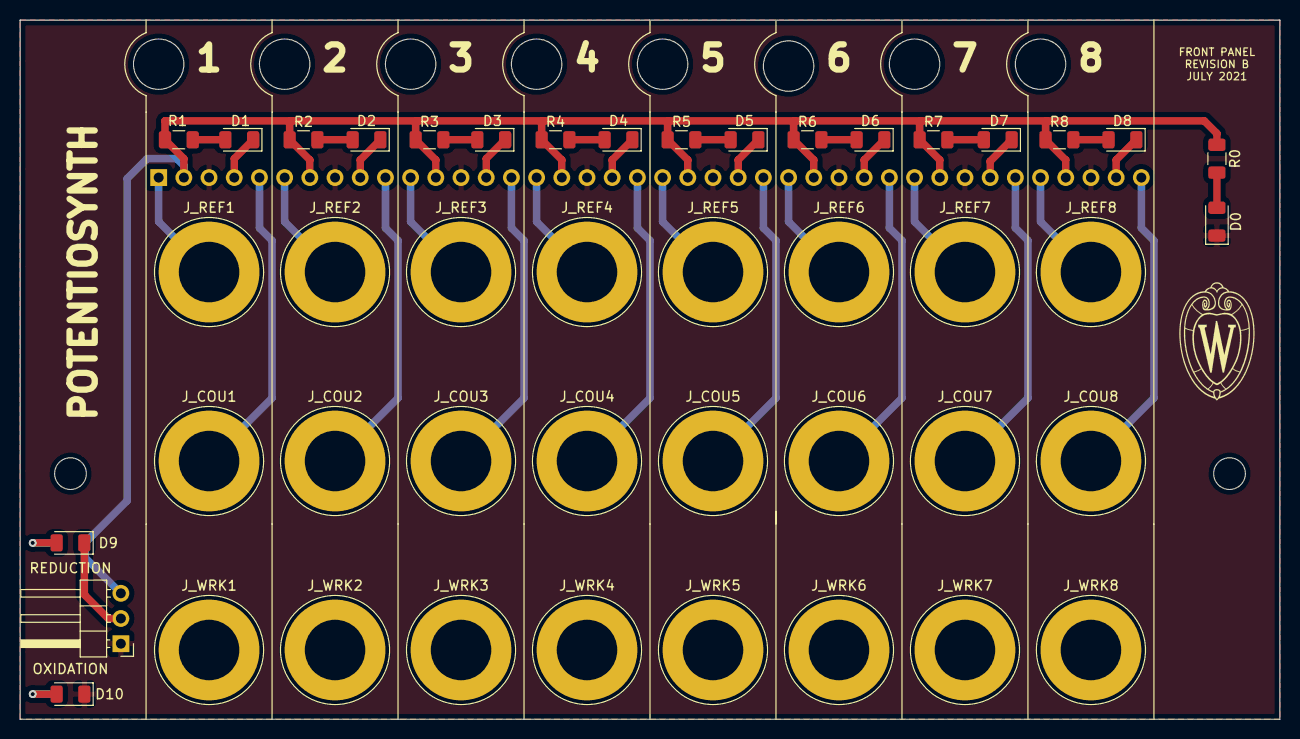
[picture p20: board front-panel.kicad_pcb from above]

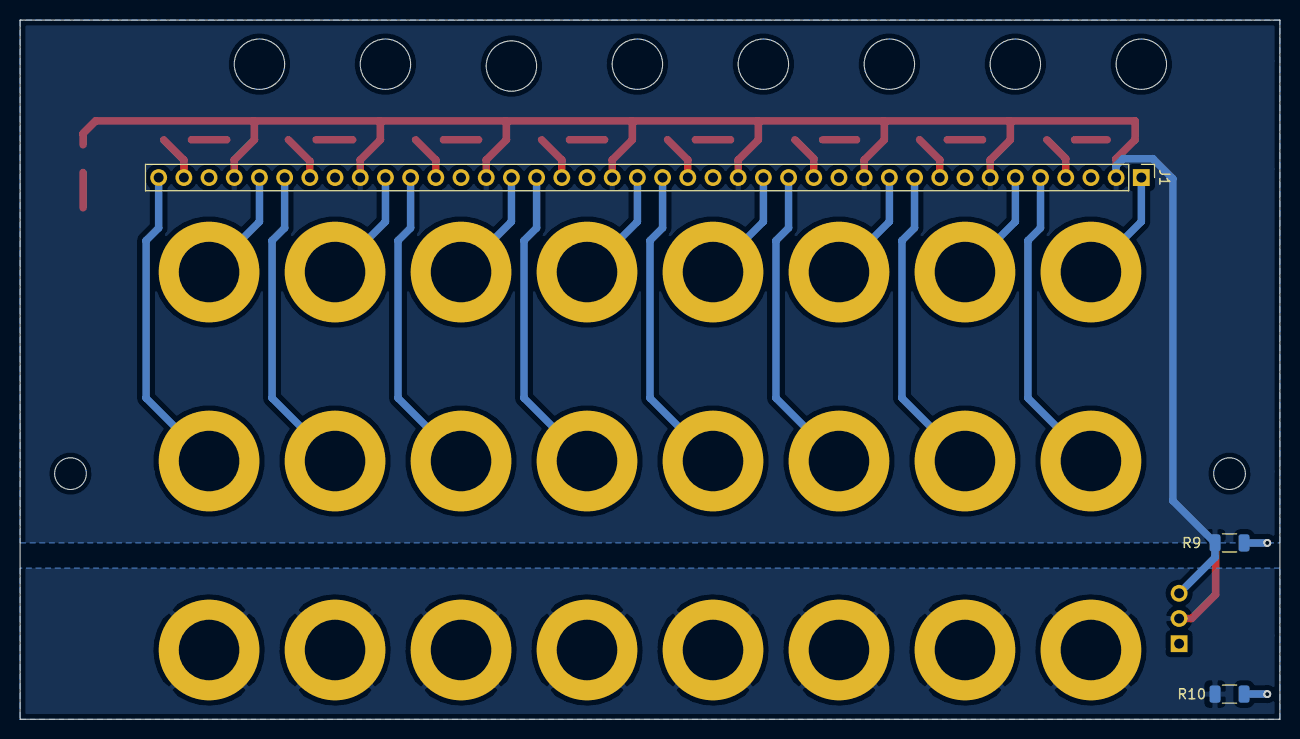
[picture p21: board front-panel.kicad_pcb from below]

Board: 2 copper layers, 127.0 x 70.5 mm, 48 parts (3 on the bottom side), 38 nets.

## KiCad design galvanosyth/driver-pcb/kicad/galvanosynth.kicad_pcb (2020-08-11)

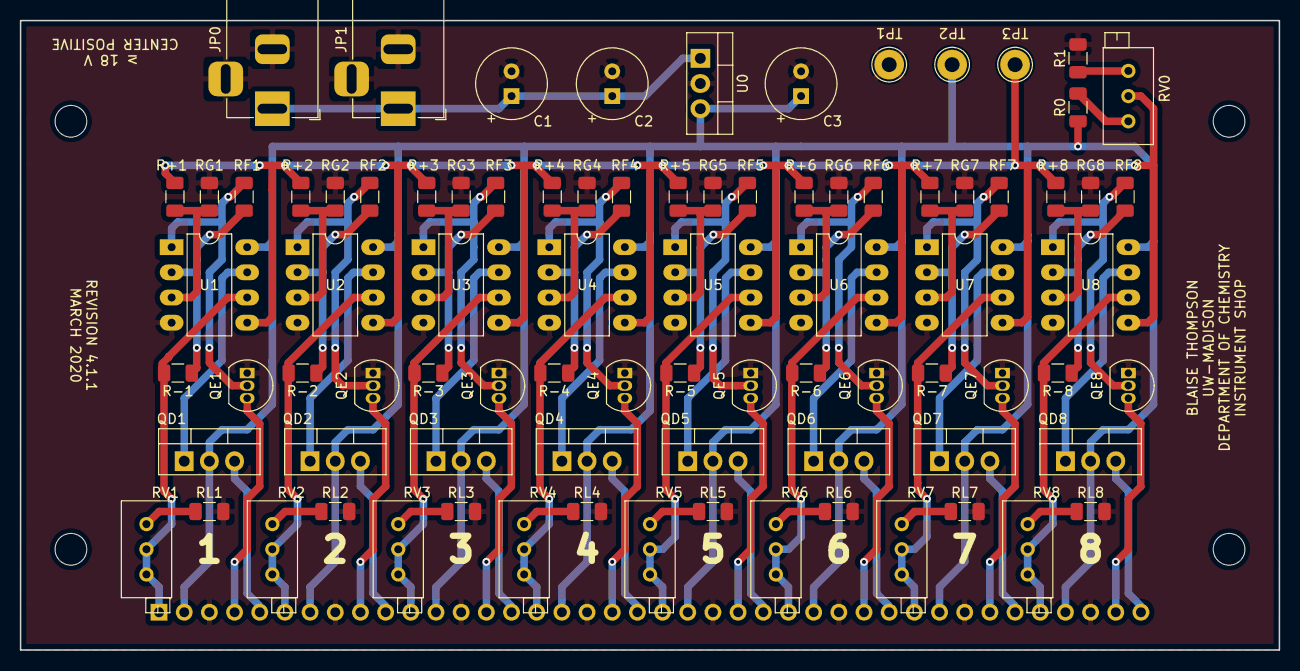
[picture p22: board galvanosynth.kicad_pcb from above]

Board: 2 copper layers, 127.0 x 63.5 mm, 85 parts (1 on the bottom side), 70 nets.

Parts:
C1: 100uF; CP_Radial_Tantal_D7.0mm_P2.50mm
C2: 330nF; CP_Radial_Tantal_D7.0mm_P2.50mm
C3: 100nF; CP_Radial_Tantal_D7.0mm_P2.50mm
J1: Conn_01x40; PinHeader_1x40_P2.54mm_Horizontal
JP0, JP1: Barrel_Jack_Switch; BarrelJack_Horizontal
QD1, QD2, QD3, QD4, QD5, QD6, QD7, QD8: IRF630; TO-220-3_Vertical
QE1, QE2, QE3, QE4, QE5, QE6, QE7, QE8: 2N7000; TO-92_Inline
R0: 10k; R_1206_3216Metric
R1: 68; R_1206_3216Metric
R+1, R+2, R+3, R+4, R+5, R+6, R+7, R+8: 1k; R_1206_3216Metric
R-1, R-2, R-3, R-4, R-5, R-6, R-7, R-8: 1k; R_1206_3216Metric
RF1, RF2, RF3, RF4, RF5, RF6, RF7, RF8: 100k; R_1206_3216Metric
RG1, RG2, RG3, RG4, RG5, RG6, RG7, RG8: 100k; R_1206_3216Metric
RL1, RL2, RL3, RL4, RL5, RL6, RL7, RL8: 10; R_1206_3216Metric
RV0: 1k; Potentiometer_Bourns_3296X_Horizontal
RV1, RV2, RV3, RV4, RV5, RV6, RV7, RV8: 2k; Potentiometer_Bourns_3296X_Horizontal
TP1, TP2, TP3: TestPoint; TestPoint_THTPad_D3.0mm_Drill1.5mm
U0: L7815; TO-220-3_Vertical
U1, U2, U3, U4, U5, U6, U7, U8: LM358; DIP-8_W7.62mm_LongPads

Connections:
+15V: C3.1, J1.2, J1.7, J1.12, J1.17, J1.22, J1.27, J1.32, J1.37, QD1.2, QD2.2, QD3.2, QD4.2, QD5.2, QD6.2, QD7.2, QD8.2, R0.1, TP2.1, U0.3, U1.8, U2.8, U3.8, U4.8, U5.8, U6.8, U7.8, U8.8
/1/CONTROL: R+1.1, R+2.1, R+3.1, R+4.1, R+5.1, R+6.1, R+7.1, R+8.1, RV0.2, TP3.1, U1.5, U2.5, U3.5, U4.5, U5.5, U6.5, U7.5, U8.5
/1/ERROR: J1.4, QE1.3
/1/RETURN: J1.1, R-1.2, RV1.2, RV1.3, U1.6
/1/SUPPLY: J1.5, QD1.3
/2/ERROR: J1.9, QE2.3
/2/RETURN: J1.6, R-2.2, RV2.2, RV2.3, U2.6
/2/SUPPLY: J1.10, QD2.3
/3/ERROR: J1.14, QE3.3
/3/RETURN: J1.11, R-3.2, RV3.2, RV3.3, U3.6
/3/SUPPLY: J1.15, QD3.3
/4/ERROR: J1.19, QE4.3
/4/RETURN: J1.16, R-4.2, RV4.2, RV4.3, U4.6
/4/SUPPLY: J1.20, QD4.3
/5/ERROR: J1.24, QE5.3
/5/RETURN: J1.21, R-5.2, RV5.2, RV5.3, U5.6
/5/SUPPLY: J1.25, QD5.3
/6/ERROR: J1.29, QE6.3
/6/RETURN: J1.26, R-6.2, RV6.2, RV6.3, U6.6
/6/SUPPLY: J1.30, QD6.3
/7/ERROR: J1.34, QE7.3
/7/RETURN: J1.31, R-7.2, RV7.2, RV7.3, U7.6
/7/SUPPLY: J1.35, QD7.3
/8/ERROR: J1.39, QE8.3
/8/RETURN: J1.36, R-8.2, RV8.2, RV8.3, U8.6
/8/SUPPLY: J1.40, QD8.3
GND: C1.2, C2.2, C3.2, J1.3, J1.8, J1.13, J1.18, J1.23, J1.28, J1.33, J1.38, JP0.2, JP0.3, JP1.2, JP1.3, QE1.1, QE2.1, QE3.1, QE4.1, QE5.1, QE6.1, QE7.1, QE8.1, R1.2, RG1.2, RG2.2, RG3.2, RG4.2, RG5.2, RG6.2, RG7.2, RG8.2, RL1.1, RL2.1, RL3.1, RL4.1, RL5.1, RL6.1, RL7.1, RL8.1, TP1.1, U0.2, U1.4, U2.4, U3.4, U4.4, U5.4, U6.4, U7.4, U8.4
unnamed: C1.1, C2.1, JP0.1, JP1.1, U0.1
unnamed: QD1.1, U1.7
unnamed: QD2.1, U2.7
unnamed: QD3.1, U3.7
unnamed: QD4.1, U4.7
unnamed: QD5.1, U5.7
unnamed: QD6.1, U6.7
unnamed: QD7.1, U7.7
unnamed: QD8.1, U8.7
unnamed: QE1.2, RF1.2, U1.1
unnamed: QE2.2, RF2.2, U2.1
unnamed: QE3.2, RF3.2, U3.1
unnamed: QE4.2, RF4.2, U4.1
unnamed: QE5.2, RF5.2, U5.1
unnamed: QE6.2, RF6.2, U6.1
unnamed: QE7.2, RF7.2, U7.1
unnamed: QE8.2, RF8.2, U8.1
unnamed: R0.2, RV0.1
unnamed: R1.1, RV0.3
unnamed: R+1.2, RG1.1, U1.3
unnamed: R+2.2, RG2.1, U2.3
unnamed: R+3.2, RG3.1, U3.3
unnamed: R+4.2, RG4.1, U4.3
unnamed: R+5.2, RG5.1, U5.3
unnamed: R+6.2, RG6.1, U6.3
unnamed: R+7.2, RG7.1, U7.3
unnamed: R+8.2, RG8.1, U8.3
unnamed: R-1.1, RF1.1, U1.2
unnamed: R-2.1, RF2.1, U2.2
unnamed: R-3.1, RF3.1, U3.2
unnamed: R-4.1, RF4.1, U4.2
unnamed: R-5.1, RF5.1, U5.2
unnamed: R-6.1, RF6.1, U6.2
unnamed: R-7.1, RF7.1, U7.2
unnamed: R-8.1, RF8.1, U8.2
unnamed: RL1.2, RV1.1
unnamed: RL2.2, RV2.1
unnamed: RL3.2, RV3.1
unnamed: RL4.2, RV4.1
unnamed: RL5.2, RV5.1
unnamed: RL6.2, RV6.1
unnamed: RL7.2, RV7.1
unnamed: RL8.2, RV8.1

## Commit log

2018-11-14 2018-11-13 19:01
    [banana_L.dxf, front.dxf, galvanostat.kicad_pcb, galvanostat.sch]
2018-11-14 2018-11-14 12:00
    [_saved_galvanostat.sch, galvanostat.kicad_pcb]
2018-11-14 2018-11-14 13:05
    [_saved_galvanostat.sch, galvanostat.sch]
2019-06-11 dual to quad
    [front.dxf, galvanostat-B_Cu.gbr, galvanostat-B_Mask.gbr, galvanostat-Edge_Cuts.gbr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]
2019-06-25 revision C
    [galvanostat.kicad_pcb, galvanostat.sch]
2021-05-05 reorg potentiosynth
    [potentiosynth.kicad_pcb, potentiosynth.sch, sub.sch]
2021-05-07 restructure galvanosynth
    [active-feedback.sch, daughter-B_Cu.gbr, daughter-B_Mask.gbr, daughter-B_Paste.gbr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]
2021-05-07 galvo front panel organize
    [daughter-B_Mask.gbr, daughter-B_Paste.gbr, daughter-B_SilkS.gbr, daughter-F_Mask.gbr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]
2021-05-07 prepare for potentiosynth
    [active-feedback.sch, daughter-B_Cu.gbr, daughter-B_Mask.gbr, daughter-B_Paste.gbr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]
2021-05-07 first draft driver-pcb
    [active-feedback.sch, potentiosynth-B_Cu.gbr, potentiosynth-B_Mask.gbr, potentiosynth-B_Paste.gbr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]
2021-05-07 first draft front panel
    [100SP1T2B4M6QE.step, front-panel.kicad_pcb, front-panel.sch]
2021-07-07 added buffer amplifier
    [active-feedback.sch, front-panel-B_Cu.gbr, front-panel-B_Mask.gbr, front-panel-B_Paste.gbr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]
2021-07-07 fixed potentiosynth front panel silkscreen
    [front-panel-B_Cu.gbr, front-panel-B_Mask.gbr, front-panel-B_Paste.gbr, front-panel-B_SilkS.gbr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]
2021-07-07 forgotten fills
    [front-panel-B_Cu.gbr, front-panel-B_Mask.gbr, front-panel-B_Paste.gbr, front-panel-B_SilkS.gbr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]
2021-07-09 add fuse
    [potentiosynth-B_Cu.gbr, potentiosynth-B_Mask.gbr, potentiosynth-B_Paste.gbr, potentiosynth-Edge_Cuts.gbr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]
2021-10-08 resistor net
    [active-feedback.sch, potentiosynth.kicad_pcb]
2021-10-12 potentiosynth driver revC
    [active-feedback.sch, potentiosynth-B_Cu.gbr, potentiosynth-B_Mask.gbr, potentiosynth-B_Paste.gbr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]
2021-11-05 uncommitted changes
    [potentiosynth-B_Cu.gbr, potentiosynth-B_Mask.gbr, potentiosynth-B_Paste.gbr, potentiosynth-B_SilkS.gbr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]
2023-08-07 Bills of Materials Updated (#9)
    * Bills of Materials Update
    * Update README.md
    * Update README.md
    * Update Bill of Materials
    * Update README.md
    * Update README.md
    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

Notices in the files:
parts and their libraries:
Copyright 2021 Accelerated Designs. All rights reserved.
